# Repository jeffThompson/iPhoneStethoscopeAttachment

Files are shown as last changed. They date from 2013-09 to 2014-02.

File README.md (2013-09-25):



iPhone Stethoscope Attachment
===========================

*Note: this is the final test version, print at your own risk! The final model should be released here shortly.*

An attachment for the iPhone 4 (tested and fits) and iPhone 5 (not tested, but should fit) for recording audio from a stethoscope.

**Audio Analysis**  
Screenshots of audio waveforms and frequency analyses

**Recordings**  
Sample audio recordings of various sounds

**Rhino CAD Files**  
Original Rhino files for the 3d printed attachment

**STL Files**  
3d-printer ready files

**mHealth Paper**  
A chapter for a forthcoming book on mobile health technologies, part of Humana Press' "Methods in Molecular Biology" series

\- \- \-

\[ this project is released under [Creative Commons BY-NC-SA license](http://creativecommons.org/licenses/by-nc-sa/3.0/) - not for commercial use, but other uses [please let me know](http://www.jeffreythompson.org) \]

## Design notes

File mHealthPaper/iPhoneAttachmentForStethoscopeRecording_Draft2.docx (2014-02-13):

Author Jeff Thompson

Affiliation Assistant Professor and Program Director

Visual Art & Technology, Stevens Institute of Technology

Email mail@jeffreythompson.org

Running head “Smartphone Attachment For Stethoscope Recording”

Smartphone Attachment For Stethoscope Recording

Jeff Thompson

Abstract

With the ubiquity of smartphones and the rising technology of 3D printing, novel devices can be developed that leverage the “computer in your pocket” and rapid prototyping technologies toward scientific, medical, engineering, and creative purposes. This paper describes such a device: a simple 3D-printed extension for Apple’s iPhone that allows the sound from an off-the-shelf acoustic stethoscope to be recorded using the phone’s built-in microphone. The attachment’s digital 3D files can be easily shared, modified for similar phones and devices capable of recording audio, and in combination with 3D printing technology allow for fabrication of a durable device without need for an entire factory of expensive and specialized machining tools. It is hoped that by releasing this device as an open source set of printable files that can be downloaded and reproduced cheaply, others can make use of these developments where access to cost-prohibitive, specialized medical instruments are not available. Coupled with specialized smartphone software (“apps”), more sophisticated and automated diagnostics may also be possible on-site.

Keywords

iPhone, stethoscope, audio recording, 3D printing, STL, Shapeways, smartphone, app, sound, selective laser sintering, fused deposition modeling

1. Introduction

The following is more of a “how to” than a laboratory procedure; this is worth noting for two reasons. First, 3D printing handles much of the heavy lifting, creating the component that acts as interface between the iPhone and the stethoscope. Once printed, the component and related pieces require minimal preparation for use. Second, I am trained and work as a visual artist, and this device is born out of my creative research. The stethoscope attachment was originally conceived as a device for making interesting, experimental audio recordings. The additional use as a medical instrument provides further evidence of something I believe strongly: that research in the arts can have practical and important applications in STEM fields.

Such a device could be used for a variety of medical purposes, including remote diagnosis of cardiovascular or respiratory issues, real-time telemedicine between a specialist and a health worker in a remote or underserved region, and, with the addition of custom-written smartphone applications, performing automated, audio-based analysis for diagnosis by non-professionals. While electronic and recording stethoscopes do exist, they are very expensive (see Reference 3). Coupled with this attachment, even an inexpensive, store-bought acoustic stethoscope can make recordings sufficient for diagnosis.

The central part of the device is a 3D printed interface between the iPhone (selected because it is the most ubiquitous smartphone today, though this design could easily be adapted for other devices) and a standard acoustic stethoscope (see Figure 1). The part is 3D printed in selective laser-sintered (SLS) nylon or ABS plastic, and is friction-fit to the bottom of the phone where the microphone is located. A barbed fitting at the base of the attachment connects the stethoscope’s PVC tubing. A hole down the barb carries sound from the tubing directly into the smartphone’s microphone, the same way sound in a traditional stethoscope is passed through the earpiece into the ear.

In order to capture the full range of adult chest sounds, higher-quality stethoscope heads have two sides: the diaphragm for higher frequency sounds in the range of approximately 100–1000 Hz, and the bell for lower frequency sounds in the range of 20–100 Hz (see Reference 1). The microphone in the iPhone 4 (released in 2010) has an attenuated frequency response, as we might guess in a consumer device not intended for high-fidelity audio. However, it is capable of recording the entire frequency range outlined above, with a very flat frequency response past 200 Hz. This suggests that, as an inexpensive, portable, and very flexible device, the iPhone is very well-suited for recording the sounds from a stethoscope.

2. Materials

1. Stethoscope head with fitting for standard 3/16 – 1/4” (4.75 – 6.3mm) ID tubing.
2. Standard stethoscope tubing (single lumen), 3/8” OD, 3/16 – 1/4” (4.75 – 6.3mm) ID, at least 6” long (see Note 1).
3. 3D-printed iPhone attachment, either using a commercial service printing in laser-sintered nylon (preferable), or locally using a hard material such as ABS or PLA plastic (see Figures 2 and 3). For an overview of 3D printing technologies, see Reference 4.
4. iPhone generation 4 or above.
5. Sound recording app for iPhone such as the pre-installed “Voice Recorder.”
6. Optional: audio post-production software for filtering recordings to improve the clarity of recordings, especially of low-frequency sounds such as heartbeats; the free, open-source Audacity is an excellent option for this purpose.

3. Methods

This section describes 3D printing, assembly, and use of the stethoscope attachment. The first of these instructions describe printing the attachment using the commercial service Shapeways; if a 3D printer is available locally, the attachment can be printed using a variety of alternative methods outlined in section 3.1.b (see Notes for possible issues and further suggestions).

3.1.a. Printing The Attachment Using Shapeways’ 3D Printing Service

Shapeways, a 3D printing service based in the United States and the Netherlands, provides very high-quality printing in a variety of materials.

1. Visit the following link to order a 3D-printed version of the stethoscope attachment: http://shpws.me/oQUX.
2. Choose a material color from the “Material Options” dropdown menu – default is white (see Note 2).
3. Click the “Buy Now” button to order the printed model in the material specified (see Note 3); at time of writing, commercial printing of the attachment was approximately $30 USD.

3.1.b. Alternatively, Print Using a Local 3D Printer

Inexpensive 3D printers designed for consumer/hobbyist use such as the Makerbot or open-source RepRap may be substituted without loss of audio fidelity, though they may take more work to produce usable prints.

1. Visit the project’s GitHub repository: https://github.com/jeffthompson/iPhoneStethoscopeAttachment.
2. Download the necessary files by clicking the “Download ZIP” button in the right sidebar. This includes the printable stereolithography (STL) files, as well as supporting documents and sample recordings.
3. Print using a hard material such as ABS or PLA plastic at 100% infill; other settings will depend on model of 3D printer (see Note 4).
4. Clean and sand/file printed model as necessary for a smooth finish.

3.2. Prepare Stethoscope Tubing

A single length of flexible PVC tubing is needed to connect the chestpiece to the 3D printed attachment. This can be repurposed from an existing stethoscope or bought in bulk and cut to size (see Note 1).

1. Cut one section of stethoscope tubing using a sharp knife or scissors. If using the tubing from an existing stethoscope, cu below the fork to form a single tube. Length is variable but less than 15” (38cm) can make it difficult to maneuver; very long tubing will likely cause a reduction in the fidelity of the audio.

3.3. Assemble the Attachment

For an image of the completed assembly, see Figure 2.

1. Slide one end of the stethoscope tubing over the barb in the stethoscope head until secure.
2. Insert the other end of the stethoscope tubing over the barb at the bottom of the 3D printed attachment; the tubing should fit tightly but can be carefully removed (see Note 5). While the 3D printed parts are sturdy, care should be taken not to break the barb when attaching the tubing.
3. Slide the 3D printed attachment over the bottom of the phone; the half-circle cutout in the attachment should align with the “home” button. Slide the attachment in until the bottom of the phone hits the bottom of the 3D printed attachment (see Note 6).

3.4. Test and Record

1. Turn on the phone and launch an audio recording app like Voice Recorder (see Note 7).
2. Set your app’s settings to highest quality possible, if available. Higher sample rate and bit depth will result in higher-fidelity recordings. Avoid recording in compressed formats like MP3 if non-compressed formats such as WAV or AIFF are available.
3. Press record and test the stethoscope. Depending on your app’s sensitivity settings, loud sounds such as tapping the stethoscope head should be very clearly picked up as sharp spikes by the microphone (see Note 8).

3.5. Audio Processing and Analysis

While the recordings from the stethoscope may be used without any processing, some filtering will make the isolation of certain sounds easier, especially for automated analysis.

1. A variety of adult chest sounds can be heard with a stethoscope and can be identified by their frequency ranges. These include “low heart sounds (including first, second, and third heart sounds) from 20 to 115 Hz; medium/high heart sounds (including systolic and diastolic murmurs) from 200 to 660 Hz; vesicular (normal) breathing from 150 to 1,000 Hz; bronchial breathing from 240 to 1,000 Hz; and crepitations (crackles) greater than or equal to 750 Hz” (see Reference 1).
2. For lower frequency sounds like heartbeats, a low-pass filter may be useful for removing noise and more clearly identifying the beats; this can be applied after the recording is made, or with a custom app in real-time (see Figures 4-6).

4. Notes

1. The design of the attachment’s barb allows for some variation in the dimensions of the tubing: any tube approximately 3/16 – 1/4" (4.75 – 6.3mm) inside diameter will fit. In the interest of accessibility and cost-savings, “UV-Resistant Black PVC Tubing” can be purchased in bulk from: http://www.mcmaster.com/#5231k83/=oainxw.
2. Shapeways’ “Strong and Flexible” material is laser-sintered nylon plastic, resulting in prints that are very strong with some flexibility. Printed parts can be easily cleaned, are dishwasher safe, and are heatproof to 80C/176F. See the following link for more information: https://www.shapeways.com/materials/strong-flexible.
3. Shapeways offers a variety of other materials for printing. If you would like to experiment with materials other than the default laser-sintered nylon, you will need to download the source files from GitHub and upload them to Shapeways.
4. Depending on your printer’s method and output material, specific settings may be required for a high-quality and durable print. For Fused Deposition Modeling (FDM) printing like the MakerBot, shrinkage may also require re-engineering the model based on trial and error (such considerations are not needed for laser-sintered nylon). It is suggested that FDM printers are set to 100% infill with at least 2-3 shells for a durable print.
5. This design, with the barb extending from the bottom of the 3D printed attachment, allows for the strongest connection with the tubing. An alternative design, available on the GitHub repository, simply has a hole in the bottom of the attachment for inserting the tubing. This is less sturdy but very easy to disassemble and put back together for cleaning, storage, or customization.
6. While every effort has been taken to avoid damage to the iPhone, it should be noted that the 3D printed attachment is pressure-fit to the phone’s body. Attachments printed using Shapeways’ laser-sintered nylon and MakerBot-printed ABS plastic both left no scratches on the phone’s surface, even at a tight fit and many installations/removals. However, use at your own risk.
7. Apple’s built-in Voice Recorder app is quite adequate for basic recording, but offers little manual control. Voice Record Pro (free, https://itunes.apple.com/us/app/voice-record-pro/id546983235?mt=8) offers manual quality adjustment (the “high quality” setting is 44.1kHz/16-bit at a bitrate of 128,000) but is limited to the AAC/MP4/M4A compressed audio formats. Audio Memos ($9.99 USD with in-app upgrades, https://itunes.apple.com/us/app/audio-memos-pro/id290160980?mt=8) has a large level meter and allows recording in the uncompressed WAV format. Both apps can be set to auto-upload to Dropbox and similar cloud services.
8. Better-quality audio recording apps may have adjustable gain for microphone input. If audio level problems persist, check that the stethoscope tubing and barb of the 3D printed attachment to the iPhone microphone are not blocked.

5. References

1. J. B. Dawson, The Practitioner, 1964, 193, 315-322.
2. Faber Acoustical has conducted a variety of high-quality audio testing on the iPhone 4 and related devices, though finding data on the more recent iPhone models did not turn up any reliable testing. For details on the process and graphs of the results, see: http://blog.faberacoustical.com/2010/ios/iphone/iphone-4-audio-and-frequency-response-limitations.
3. Various stethoscope recording devices exist but are very expensive and do not include the advanced signal processing functionality that a smartphone app could. For example, the 3M Littmann electronic stethoscope costs over $300 USD: http://www.littmann.com/wps/portal/3M/en_US/3M-Littmann/stethoscope/stethoscope-catalog/catalog/~/All-3M-Products/Brands/3M-Littmann-Stethoscopes/All-Stethoscopes?N=5002683+5927679+5932256&rt=c3.
4. For an introduction to the technologies of 3D printing, see these useful guides: “What Is 3D Printing? An Overview,” 3D Printer http://www.3dprinter.net/reference/what-is-3d-printing

“3D Printing Technologies Explained,” Shapeways Blog
https://www.shapeways.com/blog/archives/1215-3d-printing-technologies-explained.html?%2Farchives%2F1215-3d-printing-technologies-explained

FIGURE CAPTIONS

Note: figures can be placed anywhere in the text, though a large version of figure #2 at the start of the chapter would be ideal. Thank you!

Fig. 1. A schematic drawing of a standard acoustic stethoscope.

Fig. 2. A CAD rendering of the 3D printed attachment, which slides tightly onto the bottom of the iPhone. Note how the sound from the stethoscope’s tube is funneled directly into the phone’s built-in microphone. Shapes like this are difficult to manufacture, making 3D printing is an ideal solution in such cases.

Fig. 3. The completed iPhone stethoscope attachment, 3D-printed in laser-sintered nylon.

Fig. 4. The waveform from an audio recording of a human heartbeat with no filter applied. While the heartbeat is visible, there is significant noise in the recording.

Fig. 5. The same recording of a human heartbeat as Figure 4 with a low-pass filter applied. The heartbeat is much more clearly visible, especially to the untrained eye.

Fig. 6. Frequency analysis of a recording of a human heartbeat with no filter applied. While the noise floor for the iPhone’s built-in microphone is rather high, the low-frequency heartbeat is still clearly visible.

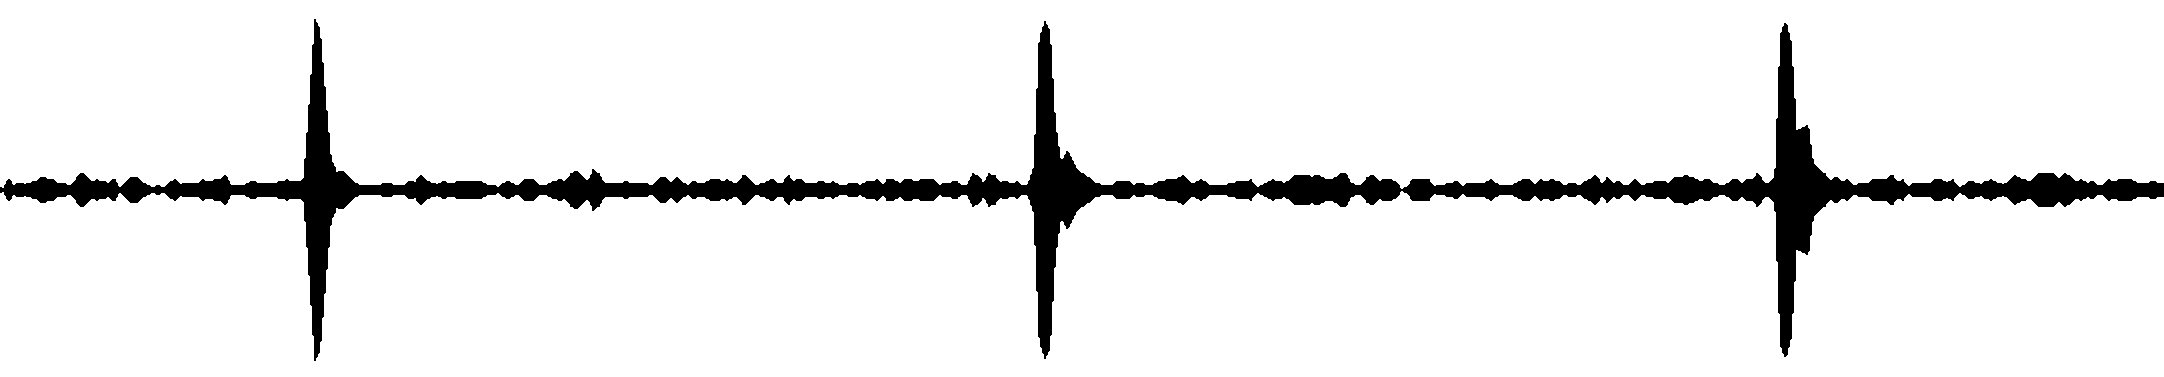
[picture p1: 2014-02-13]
mHealthPaper/Illustrations/Figure5.tif

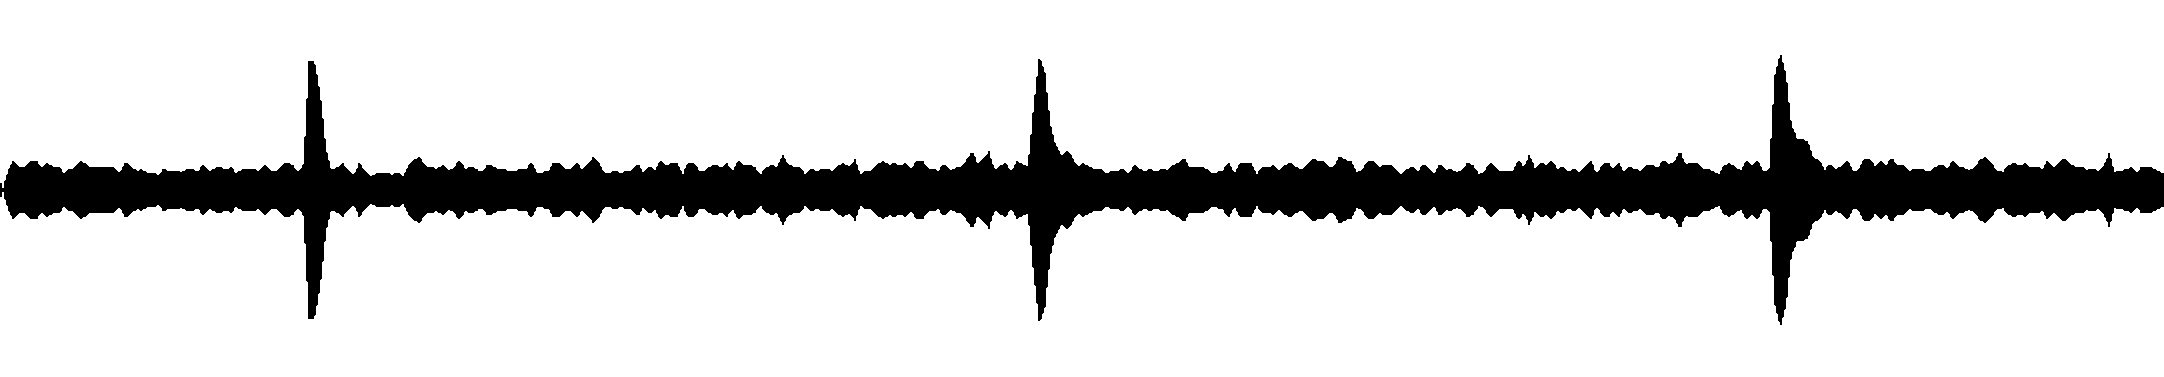
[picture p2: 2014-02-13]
mHealthPaper/Illustrations/Figure4.tif

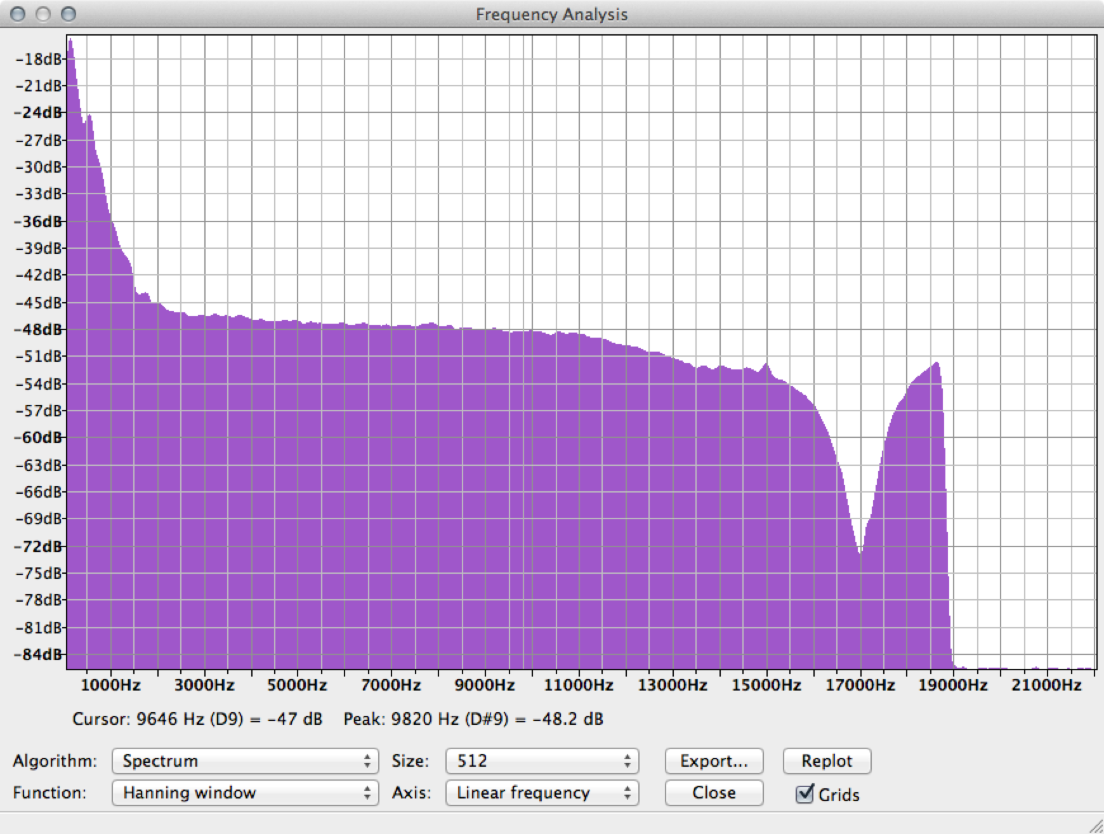
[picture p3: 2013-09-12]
mHealthPaper/Illustrations/Figure4.tiff

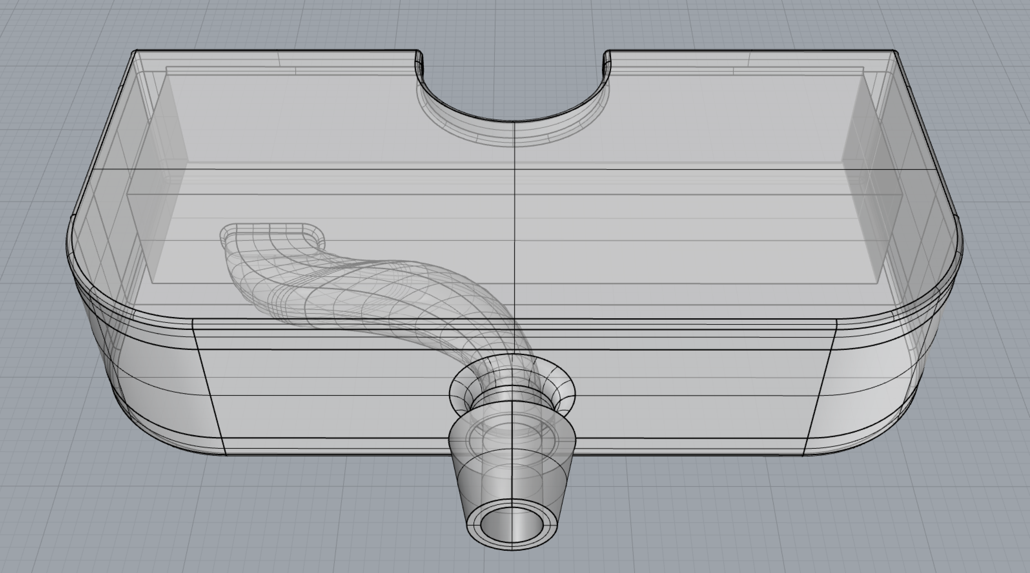
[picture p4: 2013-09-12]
mHealthPaper/Illustrations/Figure2.tiff

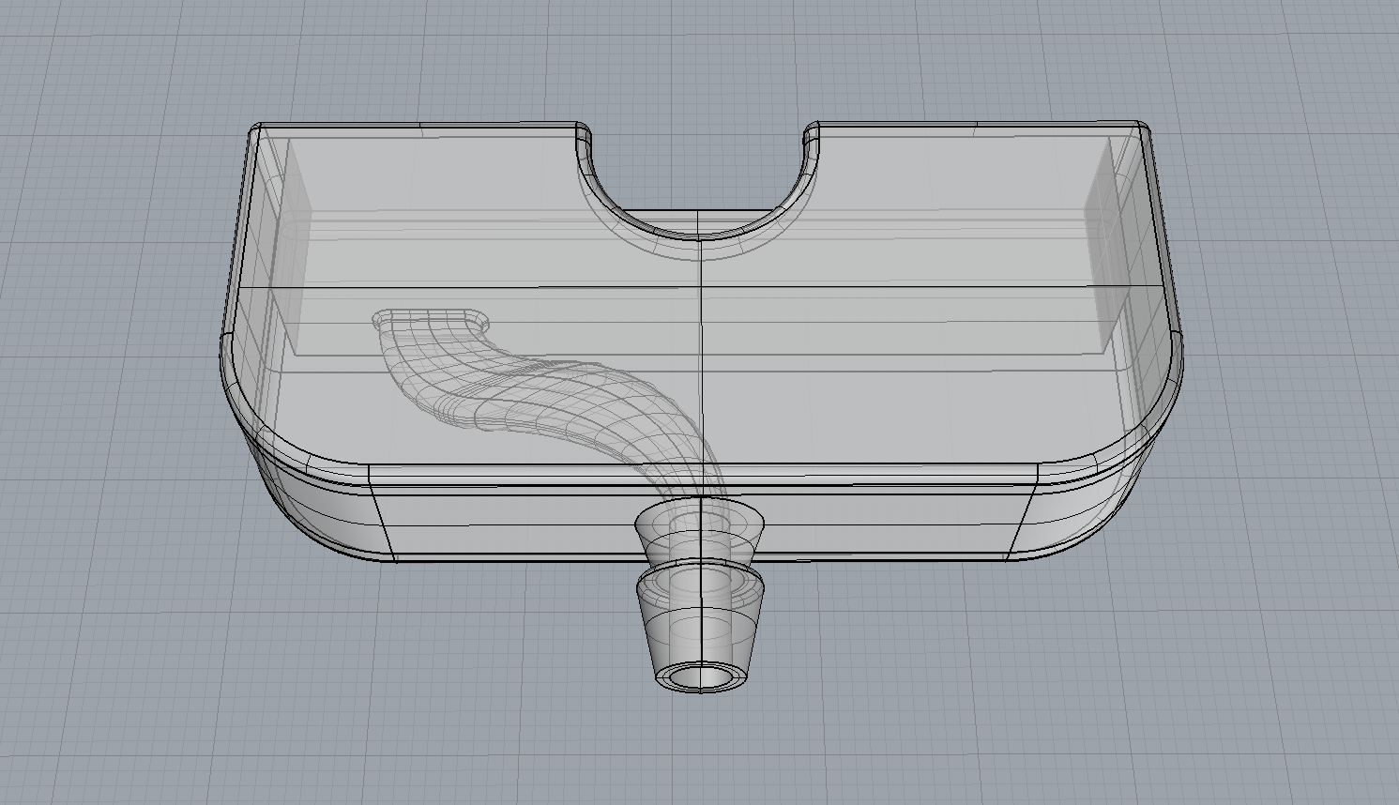
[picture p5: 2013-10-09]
Screenshot.png

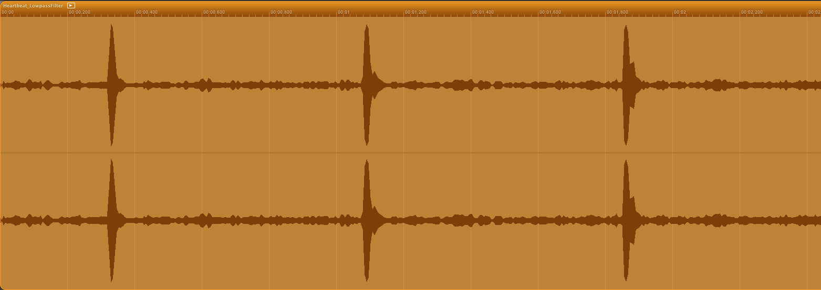
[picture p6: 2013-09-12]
AudioAnalysis/Heartbeat_LowpassStereo.png

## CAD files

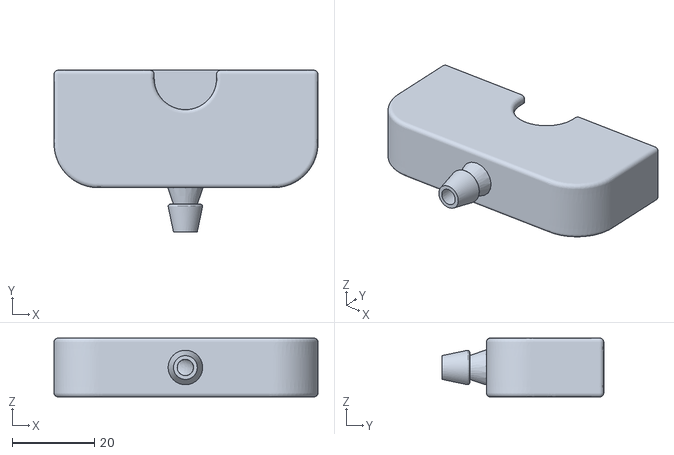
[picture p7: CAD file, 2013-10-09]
STL_Files/iPhoneStethoAttachment_wBarb.stl
64.1 x 39.2 x 14.3

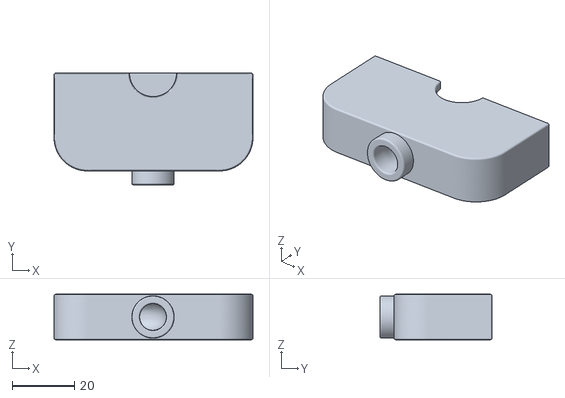
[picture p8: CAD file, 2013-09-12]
STL_Files/iPhoneStethoAttachment_wInsertHole.stl
64.1 x 36.0 x 14.6

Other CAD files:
RhinoCADFiles/iPhoneStethoAttachment_wBarb.3dm
RhinoCADFiles/iPhoneStethoAttachment_wInsertHole.3dm

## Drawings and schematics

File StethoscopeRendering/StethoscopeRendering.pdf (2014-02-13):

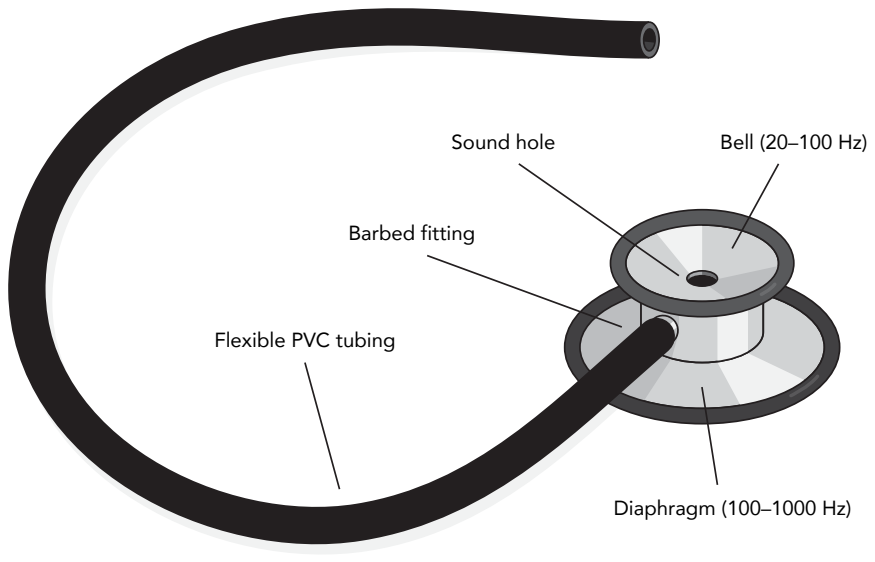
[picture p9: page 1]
Diaphragm (100–1000 Hz); Sound hole; Bell (20–100 Hz); Barbed fitting

Flexible PVC tubing

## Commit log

2013-08-09 Updated size (previously a little too tight), added brace for tube
    [iPhoneStethoAttachment_SLSprinting.3dm, iPhoneStethoAttachment_SLSprinting.stl]
2013-08-13 Enlarged for a better fit, added MiMB paper files
    [iPhoneStethoAttachment.3dm, iPhoneStethoAttachment_SLSprinting.3dm, iPhoneStethoAttachment_SLSprinting.stl, iPhoneStethoAttachment_v1.stl]
2013-09-12 Lots of paper edits, audio recordings and analysis, udpated model for barb at bottom
    [iPhoneStethoAttachment.3dm, iPhoneStethoAttachment_v1.stl, iPhoneStethoAttachment_wBarb.3dm, iPhoneStethoAttachment_wBarb.stl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]
2013-09-15 Moved Rhino CAD files to their own directory
    [iPhoneStethoAttachment_wBarb.3dm, iPhoneStethoAttachment_wInsertHole.3dm]
2013-09-25 Updated Rhino and STL model for better fit
    [iPhoneStethoAttachment_wBarb.3dm, iPhoneStethoAttachment_wBarb.stl]
2013-10-09 Updated 3d model, screenshot for height problems
    [iPhoneStethoAttachment_wBarb.3dm, iPhoneStethoAttachment_wBarb.stl]
